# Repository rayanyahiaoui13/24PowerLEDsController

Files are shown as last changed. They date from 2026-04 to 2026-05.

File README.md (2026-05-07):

# Well Illumination System

The goal of this system is to provide independent and precise control of a 24-LED matrix composed of high-power LEDs to independently illuminate 24 wells of a Greiner plate containing duckweed. This setup is integrated within a Jubilee robot architecture (a 3D printer transformed into a plant culture robot). The architecture is divided into two main stages: two dedicated PCA9685 PWM controllers that handle 12 channels each, and individual power modules equipped with AL8861 components. 

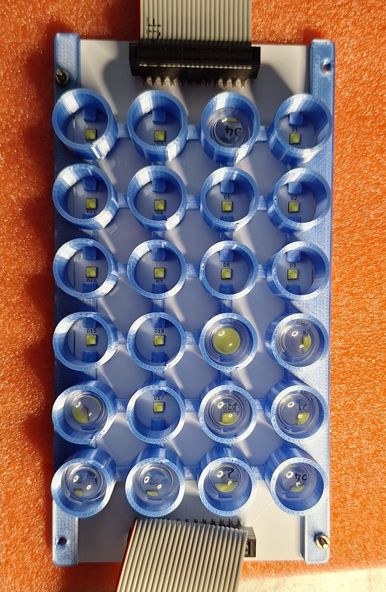
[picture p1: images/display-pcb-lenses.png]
display pcb
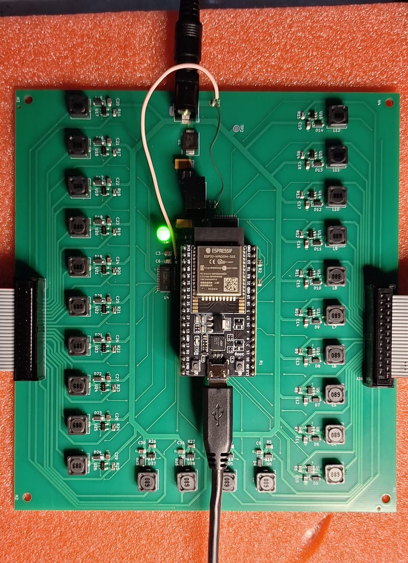
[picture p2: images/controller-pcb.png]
controller full pcb
 

## 1. 24-LED Control Board

### Power and Regulation Module
This module converts the main 12V input into a stable 3.3V supply to power the ESP32 microcontroller and the PCA9685 PWM drivers.

* **Regulator**: It uses a TSR1-2433E buck switching converter for high energy efficiency. 
* **Protection**: A D1 diode protects the circuit against reverse polarity. 
* **Diagnostics**: A green LED (D2) indicates when the system is powered. 

Voltage Regulator Module Diagram

### Microcontroller (ESP32)
The ESP32 executes the embedded program and transmits brightness instructions via I2C (SDA/SCL). Pull-up resistors (R1, R2) ensure stable data transmission. 

### PWM Drivers (PCA9685)
Two PCA9685PW chips generate 24 stable PWM signals at 400 Hz. 
* **Addressing**: Driver 1 (U3) is at 0x40; Driver 2 (U4) is at 0x41. 
* **Stability**: Decoupling capacitors (C3-C6) are placed close to the VDD pins.

### Constant Current LED Drivers (AL8861)
This power stage translates the PWM signals into constant current for the LEDs.
* **Efficiency**: Uses a Buck switching regulator to minimize heat.
* **Current Setting**: Nominal current is hardware-defined at 300 mA via a 0.33 Ω resistor (R4).

AL8861 Driver Schematic

## 2. LED Plate
This secondary PCB houses the 24 high-power OSLON SSL 80 LEDs
* **Thermal Management**: Uses an **aluminum plate** instead of standard FR4 to dissipate intense heat. 
* **Geometry**: LEDs are arranged in a matrix with 19.5 mm spacing to align with the 24-well plate. 
* **Optics**: Convergent lenses are housed in a custom 3D-printed piece to focus light.

LED Matrix Visual

## 3. Legacy Box UI (Bonus)
A 3D-printed box housing a legacy interface with a screen and rotary encoder to manually control brightness.

## Documentation & Links
* **General Git**: [science-jubilee](https://github.com/leosabatie-eng/science-jubilee)

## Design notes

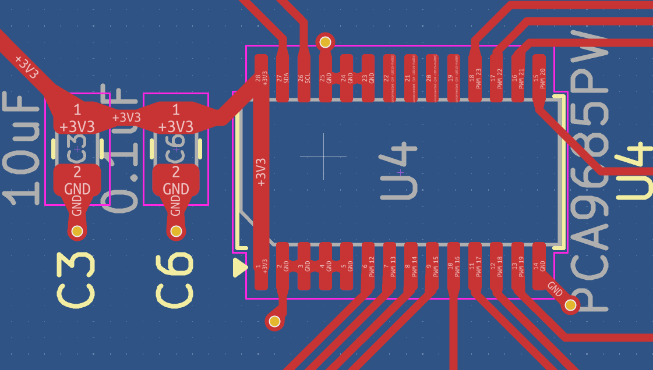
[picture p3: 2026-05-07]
images/PCA9685n2.png

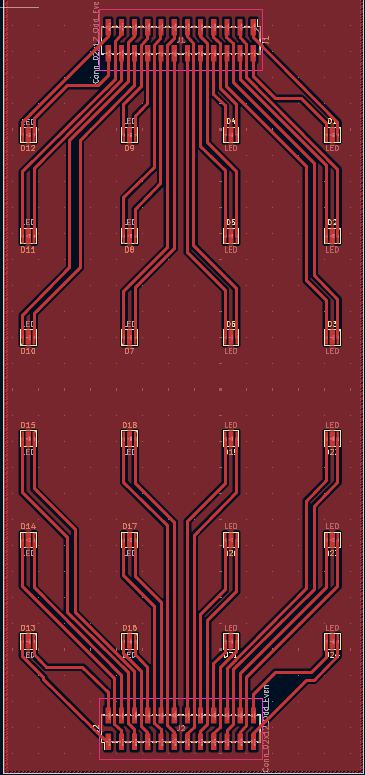
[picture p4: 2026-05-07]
images/display-kicad.png

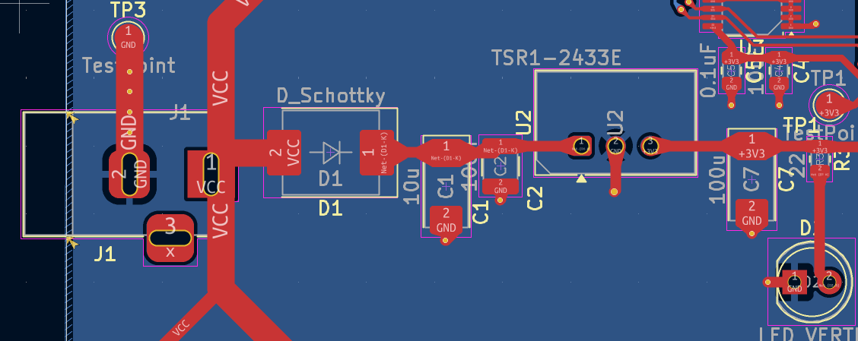
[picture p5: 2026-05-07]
images/Regulator12to3.3.png

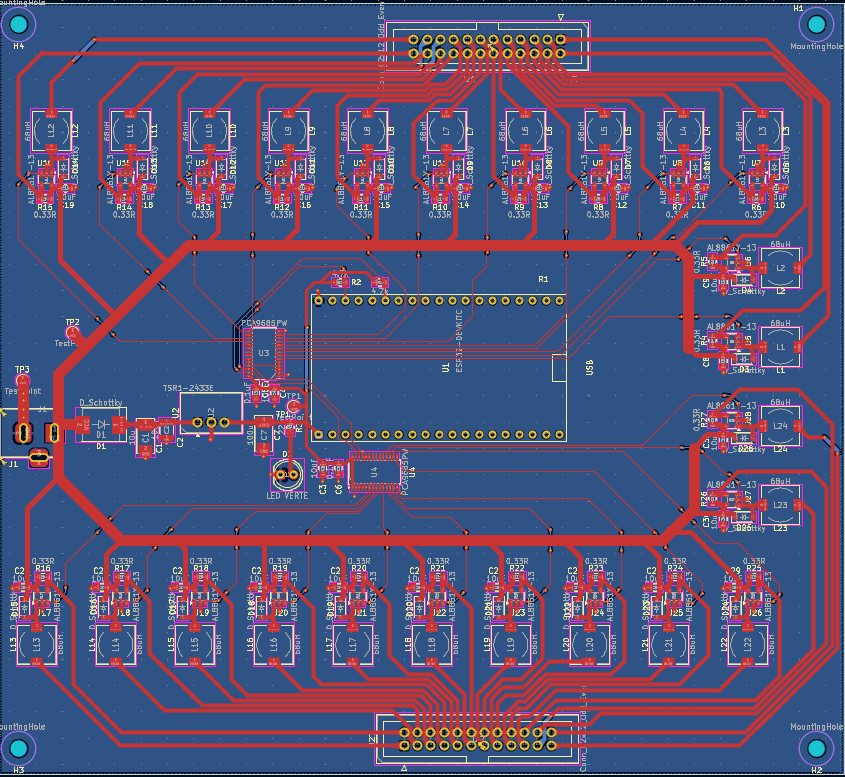
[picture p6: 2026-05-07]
images/controller-kicad.png

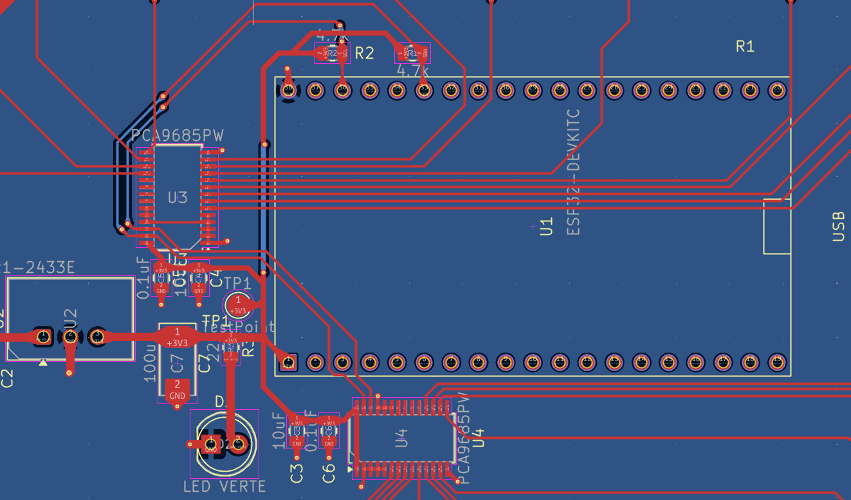
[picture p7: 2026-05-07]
images/Control-Module.png

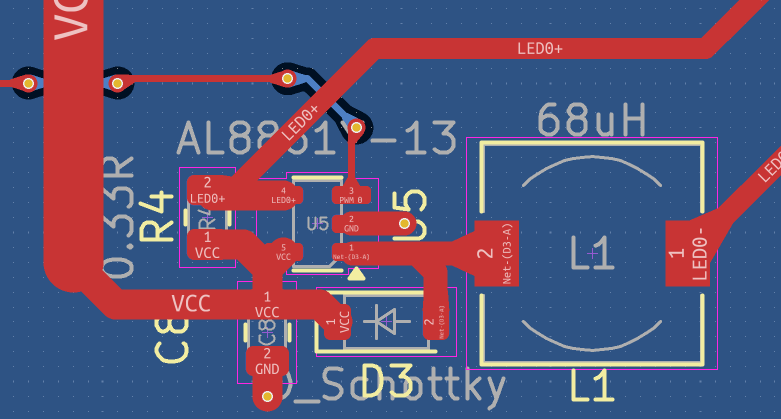
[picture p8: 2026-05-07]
images/AL8861-PowerModule.png

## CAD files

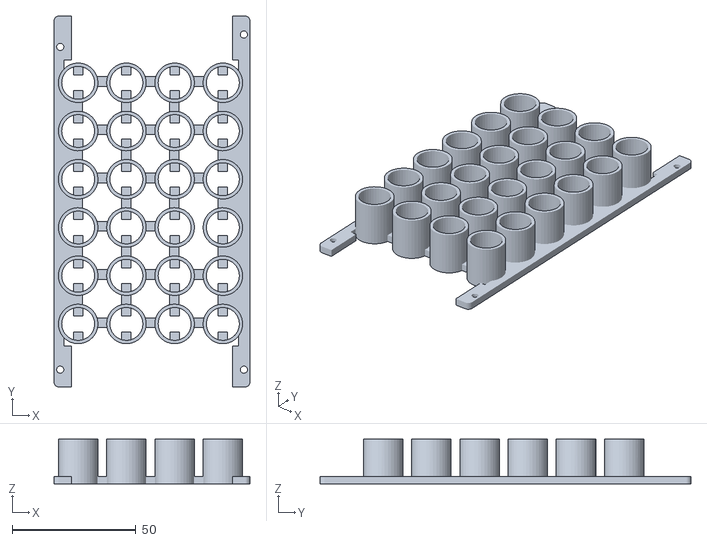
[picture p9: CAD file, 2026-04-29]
CAD-files/Pièce213led.STL
79.2 x 150.0 x 18.0

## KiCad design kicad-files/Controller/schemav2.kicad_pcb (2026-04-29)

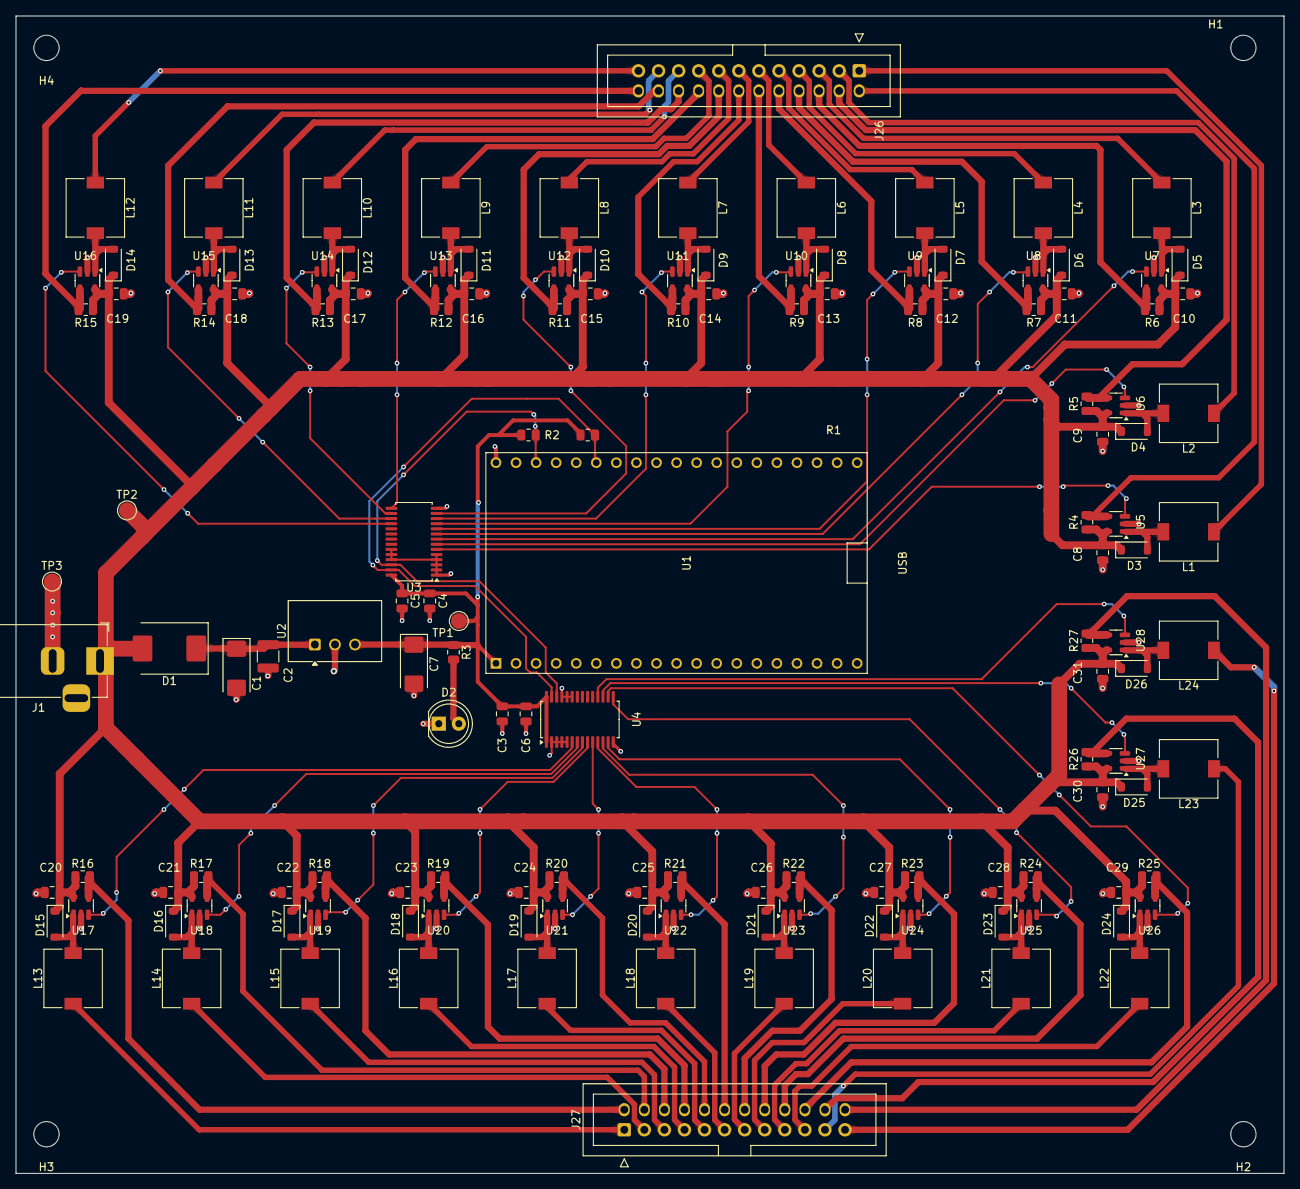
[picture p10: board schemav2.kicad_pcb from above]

Board: 2 copper layers, 160.5 x 146.5 mm, 146 parts (0 on the bottom side), 103 nets.

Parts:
C1: 10u; CP_EIA-6032-28_Kemet-C
C2: 100n; C_1210_3225Metric
C3, C4, C8, C9, C10, C11, C12, C13, C14, C15, C16, C17, C18, C19, C20, C21, C22, C23, C24, C25, C26, C27, C28, C29, C30, C31: 10uF; C_0805_2012Metric
C5, C6: 0.1uF; C_0805_2012Metric
C7: 100u; CP_EIA-6032-28_Kemet-C
D1: D_Schottky; D_SMC
D2: LED VERTE; LED_D5.0mm
D3, D4, D5, D6, D7, D8, D9, D10, D11, D12, D13, D14, D15, D16, D17, D18, D19, D20, D21, D22, D23, D24, D25, D26: D_Schottky; D_SOD-123
H1, H2, H3, H4: MountingHole; MountingHole_3.2mm_M3
J1: PJ-102AH; BarrelJack_Horizontal
J26, J27: Conn_02x12_Odd_Even; IDC-Header_2x12_P2.54mm_Vertical
L1, L2, L3, L4, L5, L6, L7, L8, L9, L10, L11, L12, L13, L14, L15, L16, L17, L18, L19, L20, L21, L22, L23, L24: 68uH; L_7.3x7.3_H4.5
R1, R2: 4.7k; R_0805_2012Metric
R3: 220; R_0805_2012Metric
R4, R5, R6, R7, R8, R9, R10, R11, R12, R13, R14, R15, R16, R17, R18, R19, R20, R21, R22, R23, R24, R25, R26, R27: 0.33R; R_0805_2012Metric
TP1, TP2, TP3: TestPoint; TestPoint_Pad_D2.0mm
U1: ESP32-DEVKITC
U2: TSR1-2433E; Converter_DCDC_TRACO_TSR1-xxxxE_THT
U3, U4: PCA9685PW; TSSOP-28_4.4x9.7mm_P0.65mm
U5, U6, U7, U8, U9, U10, U11, U12, U13, U14, U15, U16, U17, U18, U19, U20, U21, U22, U23, U24, U25, U26, U27, U28: AL8861Y-13; SOT-23-5

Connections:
+3V3: C3.1, C4.1, C5.1, C6.1, C7.1, R1.1, R2.2, R3.1, TP1.1, U1.1 (3V3), U2.3 (Vout), U3.28 (VDD), U4.1 (A0), U4.28 (VDD)
/LED0+: J26.2, R4.2, U5.4 (ISENSE)
/LED0-: J26.1, L1.1
/LED1+: J26.4, R5.2, U6.4 (ISENSE)
/LED1-: J26.3, L2.1
/LED2+: J26.6, R6.2, U7.4 (ISENSE)
/LED2-: J26.5, L3.1
/LED3+: J26.8, R7.2, U8.4 (ISENSE)
/LED3-: J26.7, L4.1
/LED4+: J26.10, R8.2, U9.4 (ISENSE)
/LED4-: J26.9, L5.1
/LED5+: J26.12, R9.2, U10.4 (ISENSE)
/LED5-: J26.11, L6.1
/LED6+: J26.14, R10.2, U11.4 (ISENSE)
/LED6-: J26.13, L7.1
/LED7+: J26.16, R11.2, U12.4 (ISENSE)
/LED7-: J26.15, L8.1
/LED8+: J26.18, R12.2, U13.4 (ISENSE)
/LED8-: J26.17, L9.1
/LED9+: J26.20, R13.2, U14.4 (ISENSE)
/LED9-: J26.19, L10.1
/LED10+: J26.22, R14.2, U15.4 (ISENSE)
/LED10-: J26.21, L11.1
/LED11+: J26.24, R15.2, U16.4 (ISENSE)
/LED11-: J26.23, L12.1
/LED12+: J27.2, R16.2, U17.4 (ISENSE)
/LED12-: J27.1, L13.1
/LED13+: J27.4, R17.2, U18.4 (ISENSE)
/LED13-: J27.3, L14.1
/LED14+: J27.6, R18.2, U19.4 (ISENSE)
/LED14-: J27.5, L15.1
/LED15+: J27.8, R19.2, U20.4 (ISENSE)
/LED15-: J27.7, L16.1
/LED16+: J27.10, R20.2, U21.4 (ISENSE)
/LED16-: J27.9, L17.1
/LED17+: J27.12, R21.2, U22.4 (ISENSE)
/LED17-: J27.11, L18.1
/LED18+: J27.14, R22.2, U23.4 (ISENSE)
/LED18-: J27.13, L19.1
/LED19+: J27.16, R23.2, U24.4 (ISENSE)
/LED19-: J27.15, L20.1
/LED20+: J27.18, R24.2, U25.4 (ISENSE)
/LED20-: J27.17, L21.1
/LED21+: J27.20, R25.2, U26.4 (ISENSE)
/LED21-: J27.19, L22.1
/LED22+: J27.22, R26.2, U27.4 (ISENSE)
/LED22-: J27.21, L23.1
/LED23+: J27.24, R27.2, U28.4 (ISENSE)
/LED23-: J27.23, L24.1
/PWM 0: U3.6 (LED0), U5.3 (VSET)
/PWM 1: U3.7 (LED1), U6.3 (VSET)
/PWM 2: U3.8 (LED2), U7.3 (VSET)
/PWM 3: U3.9 (LED3), U8.3 (VSET)
/PWM 4: U3.10 (LED4), U9.3 (VSET)
/PWM 5: U3.11 (LED5), U10.3 (VSET)
/PWM 6: U3.12 (LED6), U11.3 (VSET)
/PWM 7: U3.13 (LED7), U12.3 (VSET)
/PWM 8: U3.15 (LED8), U13.3 (VSET)
/PWM 9: U3.16 (LED9), U14.3 (VSET)
/PWM 10: U3.17 (LED10), U15.3 (VSET)
/PWM 11: U3.18 (LED11), U16.3 (VSET)
/PWM 12: U4.6 (LED0), U17.3 (VSET)
/PWM 13: U4.7 (LED1), U18.3 (VSET)
/PWM 14: U4.8 (LED2), U19.3 (VSET)
/PWM 15: U4.9 (LED3), U20.3 (VSET)
/PWM 16: U4.10 (LED4), U21.3 (VSET)
/PWM 17: U4.11 (LED5), U22.3 (VSET)
/PWM 18: U4.12 (LED6), U23.3 (VSET)
/PWM 19: U4.13 (LED7), U24.3 (VSET)
/PWM 20: U4.15 (LED8), U25.3 (VSET)
/PWM 21: U4.16 (LED9), U26.3 (VSET)
/PWM 22: U4.17 (LED10), U27.3 (VSET)
/PWM 23: U4.18 (LED11), U28.3 (VSET)
/SCL: R2.1, U1.36 (IO22), U3.26 (SCL), U4.26 (SCL)
/SDA: R1.2, U1.33 (IO21), U3.27 (SDA), U4.27 (SDA)
GND: C1.2, C2.2, C3.2, C4.2, C5.2, C6.2, C7.2, C8.2, C9.2, C10.2, C11.2, C12.2, C13.2, C14.2, C15.2, C16.2, C17.2, C18.2, C19.2, C20.2, C21.2, C22.2, C23.2, C24.2, C25.2, C26.2, C27.2, C28.2, C29.2, C30.2, C31.2, D2.1 (K), J1.2, TP3.1, U1.38 (GND3), U2.2 (GND), U3.1 (A0), U3.2 (A1), U3.3 (A2), U3.4 (A3), U3.5 (A4), U3.14 (VSS), U3.23 (~OE), U3.24 (A5), U3.25 (EXTCLK), U4.2 (A1), U4.3 (A2), U4.4 (A3), U4.5 (A4), U4.14 (VSS), U4.23 (~OE), U4.24 (A5), U4.25 (EXTCLK), U5.2 (GND), U6.2 (GND), U7.2 (GND), U8.2 (GND), U9.2 (GND), U10.2 (GND), U11.2 (GND), U12.2 (GND), U13.2 (GND), U14.2 (GND), U15.2 (GND), U16.2 (GND), U17.2 (GND), U18.2 (GND), U19.2 (GND), U20.2 (GND), U21.2 (GND), U22.2 (GND), U23.2 (GND), U24.2 (GND), U25.2 (GND), U26.2 (GND), U27.2 (GND), U28.2 (GND)
unnamed: C1.1, C2.1, D1.1 (K), U2.1 (Vin)
unnamed: D2.2 (A), R3.2
unnamed: D3.2 (A), L1.2, U5.1 (LX)
unnamed: D4.2 (A), L2.2, U6.1 (LX)
unnamed: D5.2 (A), L3.2, U7.1 (LX)
unnamed: D6.2 (A), L4.2, U8.1 (LX)
unnamed: D7.2 (A), L5.2, U9.1 (LX)
unnamed: D8.2 (A), L6.2, U10.1 (LX)
unnamed: D9.2 (A), L7.2, U11.1 (LX)
unnamed: D10.2 (A), L8.2, U12.1 (LX)
unnamed: D11.2 (A), L9.2, U13.1 (LX)
unnamed: D12.2 (A), L10.2, U14.1 (LX)
unnamed: D13.2 (A), L11.2, U15.1 (LX)
unnamed: D14.2 (A), L12.2, U16.1 (LX)
unnamed: D15.2 (A), L13.2, U17.1 (LX)
unnamed: D16.2 (A), L14.2, U18.1 (LX)
unnamed: D17.2 (A), L15.2, U19.1 (LX)
unnamed: D18.2 (A), L16.2, U20.1 (LX)
unnamed: D19.2 (A), L17.2, U21.1 (LX)
unnamed: D20.2 (A), L18.2, U22.1 (LX)
unnamed: D21.2 (A), L19.2, U23.1 (LX)
unnamed: D22.2 (A), L20.2, U24.1 (LX)
unnamed: D23.2 (A), L21.2, U25.1 (LX)
unnamed: D24.2 (A), L22.2, U26.1 (LX)
unnamed: D25.2 (A), L23.2, U27.1 (LX)
unnamed: D26.2 (A), L24.2, U28.1 (LX)
VCC: C8.1, C9.1, C10.1, C11.1, C12.1, C13.1, C14.1, C15.1, C16.1, C17.1, C18.1, C19.1, C20.1, C21.1, C22.1, C23.1, C24.1, C25.1, C26.1, C27.1, C28.1, C29.1, C30.1, C31.1, D1.2 (A), D3.1 (K), D4.1 (K), D5.1 (K), D6.1 (K), D7.1 (K), D8.1 (K), D9.1 (K), D10.1 (K), D11.1 (K), D12.1 (K), D13.1 (K), D14.1 (K), D15.1 (K), D16.1 (K), D17.1 (K), D18.1 (K), D19.1 (K), D20.1 (K), D21.1 (K), D22.1 (K), D23.1 (K), D24.1 (K), D25.1 (K), D26.1 (K), J1.1, R4.1, R5.1, R6.1, R7.1, R8.1, R9.1, R10.1, R11.1, R12.1, R13.1, R14.1, R15.1, R16.1, R17.1, R18.1, R19.1, R20.1, R21.1, R22.1, R23.1, R24.1, R25.1, R26.1, R27.1, TP2.1, U5.5 (VIN), U6.5 (VIN), U7.5 (VIN), U8.5 (VIN), U9.5 (VIN), U10.5 (VIN), U11.5 (VIN), U12.5 (VIN), U13.5 (VIN), U14.5 (VIN), U15.5 (VIN), U16.5 (VIN), U17.5 (VIN), U18.5 (VIN), U19.5 (VIN), U20.5 (VIN), U21.5 (VIN), U22.5 (VIN), U23.5 (VIN), U24.5 (VIN), U25.5 (VIN), U26.5 (VIN), U27.5 (VIN), U28.5 (VIN)

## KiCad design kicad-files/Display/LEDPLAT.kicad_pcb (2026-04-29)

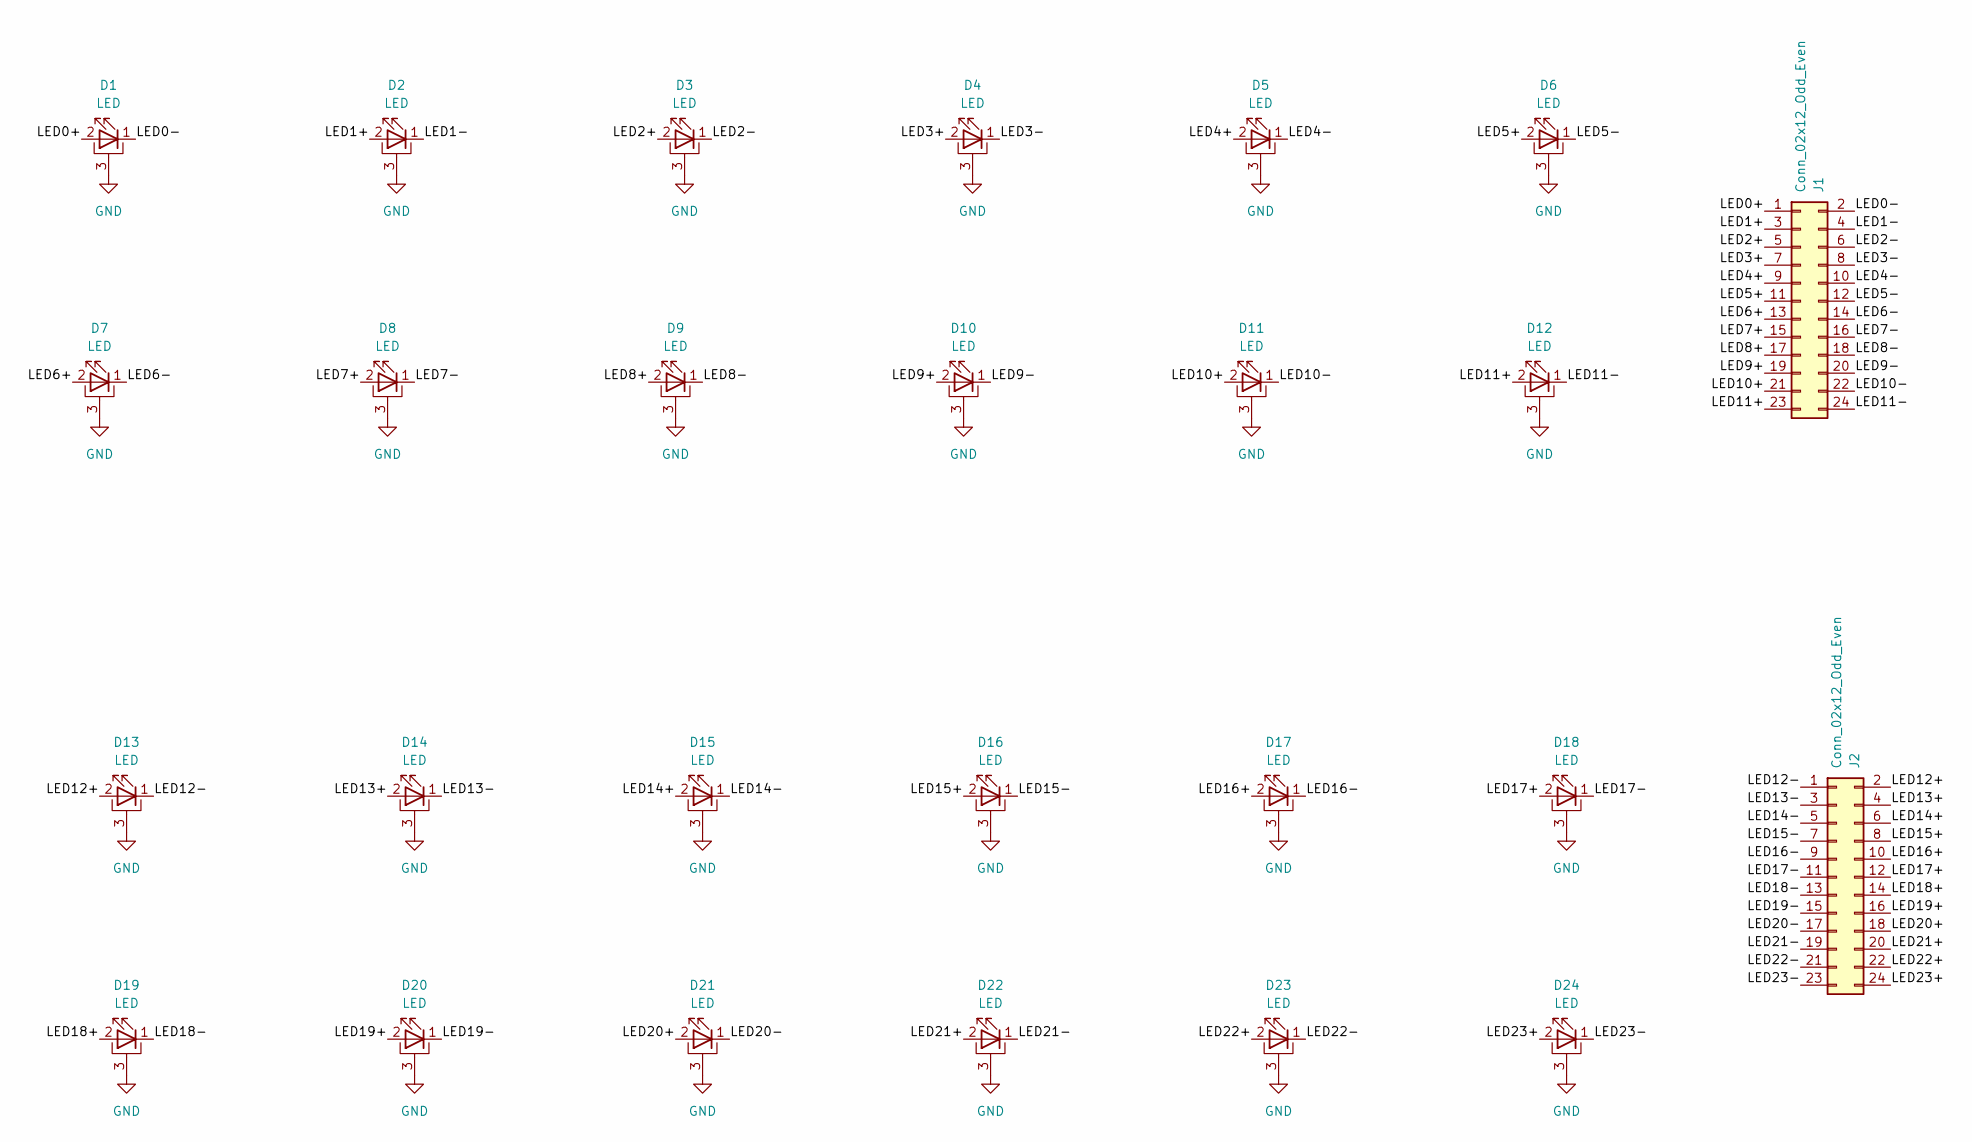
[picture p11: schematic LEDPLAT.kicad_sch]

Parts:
D1, D2, D3, D4, D5, D6, D7, D8, D9, D10, D11, D12, D13, D14, D15, D16, D17, D18, D19, D20, D21, D22, D23, D24: LED; LED_OSLON_SSL80
J1, J2: Conn_02x12_Odd_Even; PinHeader_2x12_P2.54mm_Vertical_SMD

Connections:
/LED0+: D1.2 (A), J1.1
/LED0-: D1.1 (K), J1.2
/LED1+: D2.2 (A), J1.3
/LED1-: D2.1 (K), J1.4
/LED2+: D3.2 (A), J1.5
/LED2-: D3.1 (K), J1.6
/LED3+: D4.2 (A), J1.7
/LED3-: D4.1 (K), J1.8
/LED4+: D5.2 (A), J1.9
/LED4-: D5.1 (K), J1.10
/LED5+: D6.2 (A), J1.11
/LED5-: D6.1 (K), J1.12
/LED6+: D7.2 (A), J1.13
/LED6-: D7.1 (K), J1.14
/LED7+: D8.2 (A), J1.15
/LED7-: D8.1 (K), J1.16
/LED8+: D9.2 (A), J1.17
/LED8-: D9.1 (K), J1.18
/LED9+: D10.2 (A), J1.19
/LED9-: D10.1 (K), J1.20
/LED10+: D11.2 (A), J1.21
/LED10-: D11.1 (K), J1.22
/LED11+: D12.2 (A), J1.23
/LED11-: D12.1 (K), J1.24
/LED12+: D13.2 (A), J2.2
/LED12-: D13.1 (K), J2.1
/LED13+: D14.2 (A), J2.4
/LED13-: D14.1 (K), J2.3
/LED14+: D15.2 (A), J2.6
/LED14-: D15.1 (K), J2.5
/LED15+: D16.2 (A), J2.8
/LED15-: D16.1 (K), J2.7
/LED16+: D17.2 (A), J2.10
/LED16-: D17.1 (K), J2.9
/LED17+: D18.2 (A), J2.12
/LED17-: D18.1 (K), J2.11
/LED18+: D19.2 (A), J2.14
/LED18-: D19.1 (K), J2.13
/LED19+: D20.2 (A), J2.16
/LED19-: D20.1 (K), J2.15
/LED20+: D21.2 (A), J2.18
/LED20-: D21.1 (K), J2.17
/LED21+: D22.2 (A), J2.20
/LED21-: D22.1 (K), J2.19
/LED22+: D23.2 (A), J2.22
/LED22-: D23.1 (K), J2.21
/LED23+: D24.2 (A), J2.24
/LED23-: D24.1 (K), J2.23
GND: D1.3 (PAD), D2.3 (PAD), D3.3 (PAD), D4.3 (PAD), D5.3 (PAD), D6.3 (PAD), D7.3 (PAD), D8.3 (PAD), D9.3 (PAD), D10.3 (PAD), D11.3 (PAD), D12.3 (PAD), D13.3 (PAD), D14.3 (PAD), D15.3 (PAD), D16.3 (PAD), D17.3 (PAD), D18.3 (PAD), D19.3 (PAD), D20.3 (PAD), D21.3 (PAD), D22.3 (PAD), D23.3 (PAD), D24.3 (PAD)

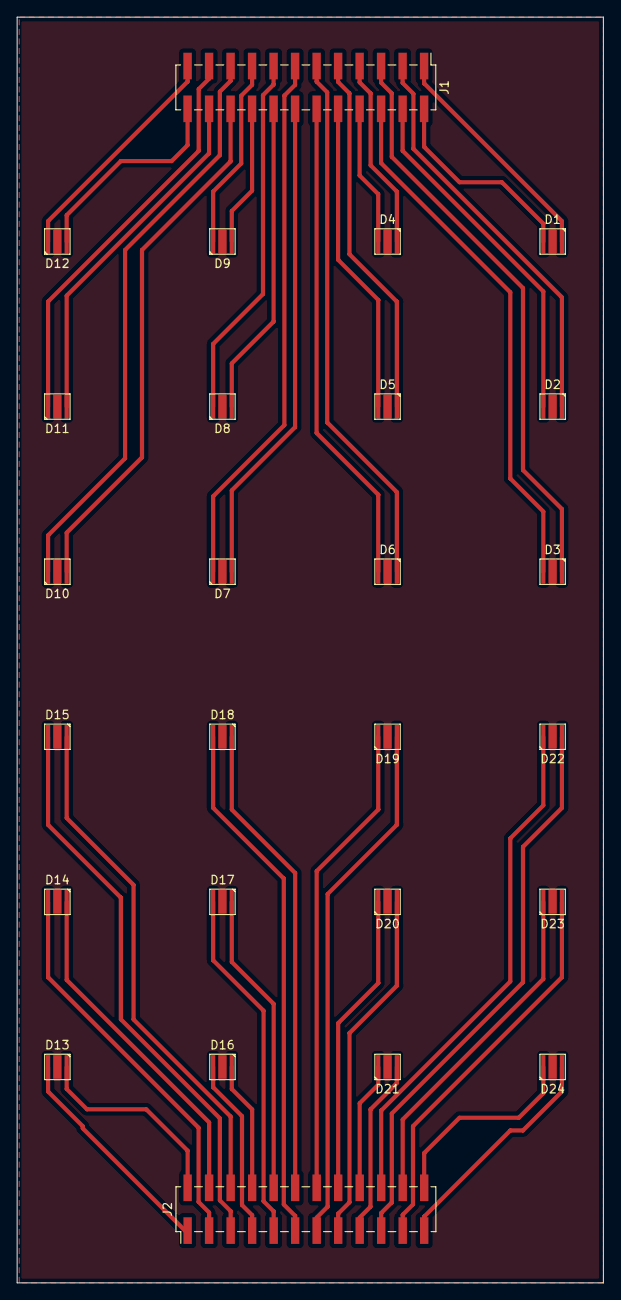
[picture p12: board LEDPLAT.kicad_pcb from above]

Board: 2 copper layers, 69.2 x 149.5 mm, 26 parts (0 on the bottom side), 49 nets.

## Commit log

2026-05-05 Add README for Well Illumination System
    Added detailed documentation for the Well Illumination System, including descriptions of the control board, power modules, and LED plate.
2026-05-07 Add controller PCB image to README
    Added an image of the controller PCB to the README.
2026-05-07 Change image in README from display to controller PCB
    Updated image references in the README for clarity.
